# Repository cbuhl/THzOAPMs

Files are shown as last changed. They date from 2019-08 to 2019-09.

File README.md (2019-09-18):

# Rapid Prototyping of Simple Optical Elements for the Terahertz Domain
By [Christian Buhl Sørensen](https://vbn.aau.dk/en/persons/139637) (Presenting author), [Anders Faarbæk Mikkelstrup](https://vbn.aau.dk/en/persons/143999) and [Esben Skovsen](https://vbn.aau.dk/en/persons/113858).

This repository provides easy access to the supporting content of the poster presented on the IRMMW-THz conference in Paris, 2019. The entire repository is supplied as inspiration and a starting point. You are exceedingly welcome to fork and extend the work shown here.

I do not guarantee the longevity of the information provided here, so if you like it - fork it! :dancer:

## Contents

The repository contains the poster (RapidPrototyping.pdf), a folder with the data analysis for the dimensional qualification, as well as a folder with STL sample files. Furthermore the repository contains supporting documentation such as this readme file, the license under which it is published, and images for the tacky tack-on badge.

## STL sample files
The STL files folder contains three relevant files as of now:
 - **45degMountV1.stl**: The mounting element for the V1 of the mirrors. Note that the angles on the mirror interface are not compatible with the V2 mirror. The central flat on the edge should be a smidge longer than 32mm, and the angle between the flat and the facet surfaces should be 140deg, included angle. This means the included angle on the facets should be 100deg, with at least 32 mm between for solid 3-surface mounting. The mating facet on the mount is 10mm high. 
 - **d100mm_efl150mm_V1.stl**: Version 1, a simple model of an off-axis parabolic mirror. 
 - **d100mm_efl150mm_V2.stl**: This version does not print well. The added reference cut-outs are an absolute godsend during alignment, and should be included on all coming designs, but the ribs on the backside are not functional. It is more relevant to print at a lower infill, to save weight at the end. Or just not print the ribs. Furthermore, the angles on the mating surfaces does not match up with the V1 mount.
 - **d100mm_efl150mm_V3.stl**: Version 3, without ribbing on the backside. This should print better. It still includes the alignment lines. Furthermore the geometry has been made compatible with the V1 mount.
 
### Suggestions for printing parameters
The printing should be straight-forward, but there are a few tricks;
 - Ensure that the shell-thickness is 2mm or higher. You need the stiffness of the outer shell, to polish it sucessfully. 
 - The infill has not been found critical. The shown mirrors are printed at 20%. 
 - PLA is the only material that has been tried. A slightly harder variety (PLA-max) has been used with success.
 - Generally low transverse printing speeds have been applied. 100mm/s or less on an ultimaker 3.
 - A 0.4mm nozzle diameter, with 0.2mm layer height has been used. The nozzle diameter should not be critical, as the transverse geometry is smooth on the optically relevant surfaces. The layer height should be kept low - this is the main contribution to the local surface roughness.

## Data analysis for the dimensional qualification
The folder contains two notebooks, and an exported binary file describing the error in motion referenced to the best fit plane. 
 
 - **20190815 Fitting Flat Plane.ipynb** shows the fit procedure and estimates the error in measurement of a flat plane.
 - **20190816 OAPM fit.ipynb** shows the fit procedure to the theoretical polynomial.
 
Note that the data analysis is just that - don't expect beautiful, lucid code. I'm more than willing to answer questions that you may have, but note that the data analysis is added just for reference.

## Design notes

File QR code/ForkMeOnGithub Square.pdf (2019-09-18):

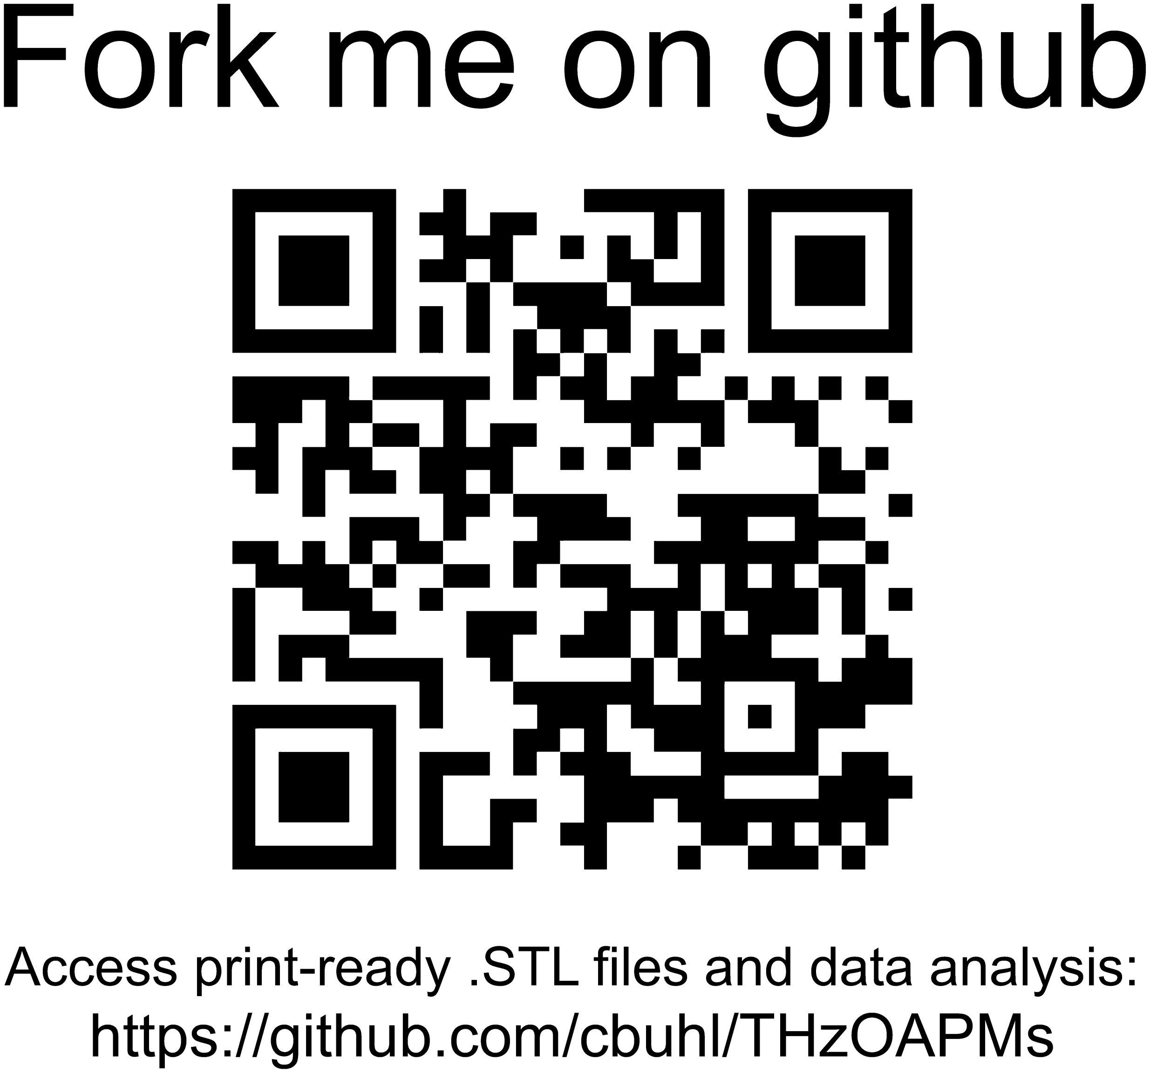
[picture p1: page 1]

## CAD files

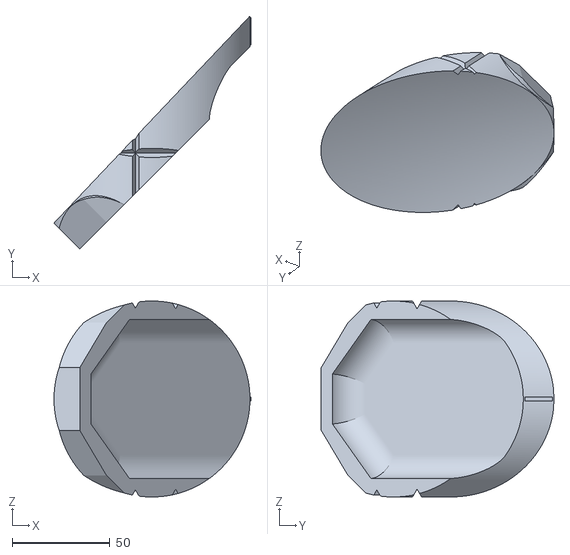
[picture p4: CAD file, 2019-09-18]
STL files/d100mm_efl150mm_V3.stl
100.5 x 118.7 x 100.0

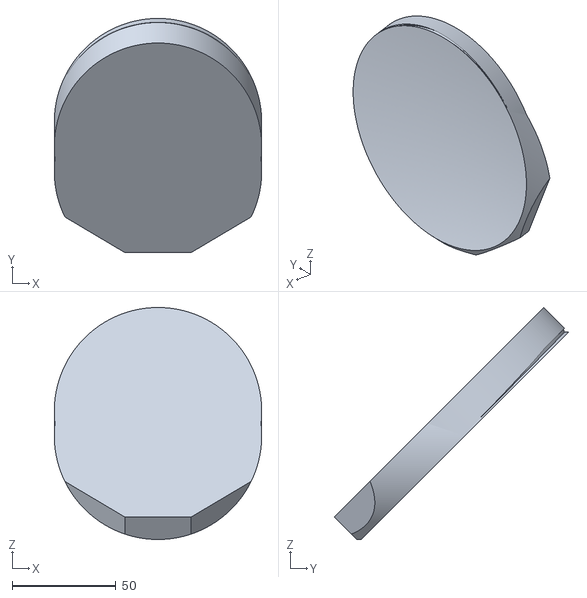
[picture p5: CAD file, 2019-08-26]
STL files/d100mm_efl150mm_V1.stl
100.0 x 112.9 x 111.9

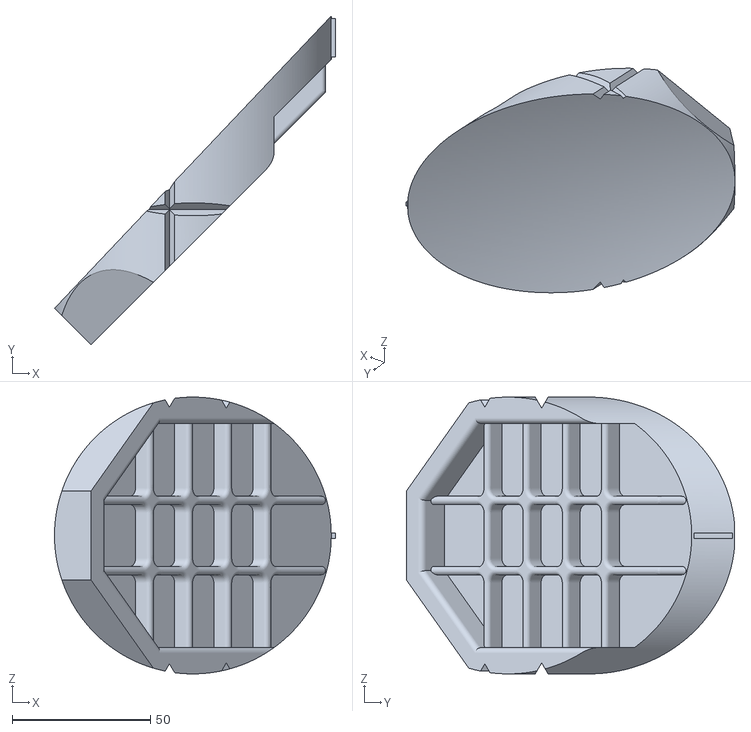
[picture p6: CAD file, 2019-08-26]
STL files/d100mm_efl150mm_V2.stl
101.5 x 118.7 x 100.0

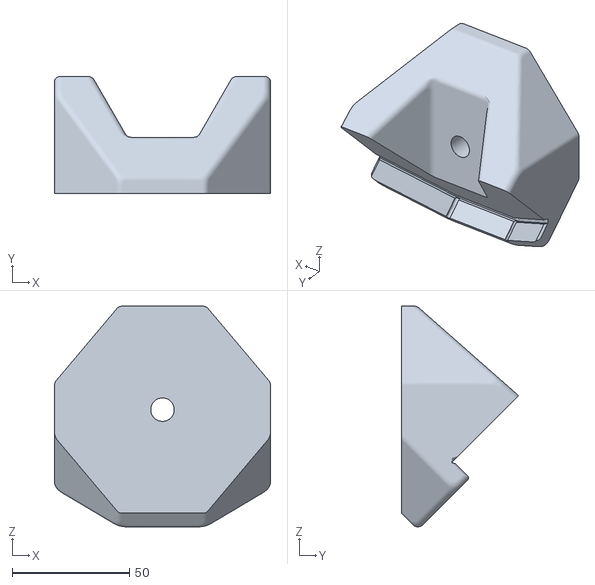
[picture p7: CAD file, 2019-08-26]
STL files/45degMountV1.stl
92.0 x 50.0 x 94.0

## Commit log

2019-08-26 Initial commit of files
    [45degMountV1.stl, Ø100_150RFL_V2.stl, Ø100_flat_150mmRFL.stl]
2019-08-26 Changed names on mirrors
    [d100mm_efl150mm_V1.stl, d100mm_efl150mm_V2.stl]
2019-09-03 Added details on printing parameters
2019-09-18 Added version 3 of mirror - now without backside ribbing and with compatibility to the mount
    [Ø100_150RFL_V3.stl]
2019-09-18 Update to reflect naming convention
    [d100mm_efl150mm_V3.stl]
2019-09-18 Updated to include new mirror
    as well as comments on the facet geometry for mounting.
